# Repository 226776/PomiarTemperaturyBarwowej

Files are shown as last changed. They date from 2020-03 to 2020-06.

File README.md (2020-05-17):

# Pomiar Temperatury Barwowej

## Opis:
Realizacja systemu do pomiaru temperatury bawowej źródeł światła. 
Na system pomiarowy składać się będą: 
- Układ akwizycji danych 
- PC 
- Oprogramowanie 

## Założenia konstrukcyjne:
- metodologia pomiaru: badanie składowych RGB i porównanie ich z charakterystyką ciała doskonale czarnego
- dokładność +-500K
- kalkulacja oraz prezentacja wyniku realizowana przez skrypt/program na PC 
- realizacja układu akwizycji przy użyciu mikrokontrolera z wbudowanym modułem ADC
- zasilanie układu awizycji danych: USB 5V

## Schematic 
- Status: zweryfikowany - płytka wytrawiona
- Środowisko: eagle

## Podgląd
View1
View1

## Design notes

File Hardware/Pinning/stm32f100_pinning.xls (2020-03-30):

PIN | PIN NAME | PIN TYPE | SIGNAL | OPIS | MCU model | Obudowa
1 | Vbat | S | +3V3 | +3V3 | STM32F100C8T6B | LGFP48
2 | PC13-TAMPER-RTC | I/O
3 | PC14-OSC32_IN | I/O
4 | PC15-OSC32_OUT | I/O
5 | OSC_IN | I/O
6 | OSC_OUT | I/O
7 | NRST | I | RESET | Podciągnąc od +3V3. Można dać jakiś przycisk do resetu
8 | Vssa | S | GND | Zasilanie części analogowej GND
9 | Vdda | S | +3V3 | Zasilanie części analogowej +3V3
10 | PA0-WKUP | I/O
11 | PA1 | I/O |  | ANALOG
12 | PA2 | I/O | TX | USART2_TX - wyprowadzenie na goldpiny
13 | PA3 | I/O | RX | USART2_RX - wyprowadzenie na goldpiny
14 | PA4 | I/O | TCSx_OUT | OUT - pin wyjściowy z czujnika TCS3200D
15 | PA5 | I/O |  | ANALOG
16 | PA6 | I/O |  | ANALOG
17 | PA7 | I/O |  | ANALOG
18 | PB0 | I/O |  | ANALOG
19 | PB1 | I/O |  | ANALOG
20 | PB2 | I/O | BOOT1 | BOOT1 - podłączyć przez 1kΩ do GND
21 | PB10 | I/O
22 | PB11 | I/O
23 | Vss_1 | S | GND | GND
24 | Vdd_1 | S | +3V3 | +3V3
25 | PB12 | I/O
26 | PB13 | I/O
27 | PB14 | I/O
28 | PB15 | I/O
29 | PA8 | I/O
30 | PA9 | I/O |  | USART1_TX - można gdzieś wyprowadzić do bootloadera
31 | PA10 | I/O |  | USART1_RX - można gdzieś wyprowadzić do bootloadera
32 | PA11 | I/O
33 | PA12 | I/O
34 | PA13 | I/O | SWDIO | SWDIO - linia danych do programowania. Wyprowadzić na goldpiny
35 | Vss_2 | S | GND | GND
36 | Vdd_2 | S | +3V3 | +3V3
37 | PA14 | I/O | SWCLK | SWCLK - linia zegarowa do programowania. Wyprowadzić na goldpiny
38 | PA15 | I/O
39 | PB3 | I/O
40 | PB4 | I/O
41 | PB5 | I/O | /OE | /OE - pin czujnika TCS3200D
42 | PB6 | I/O | S0 | S0 - pin czujnika TCS3200D
43 | PB7 | I/O | S1 | S1 - pin czujnika TCS3200D
44 | BOOT0 | I | BOOT0 | BOOT0 - podłączyć przez 1kΩ do GND
45 | PB8 | I/O | S2 | S2 - pin czujnika TCS3200D
46 | PB9 | I/O | S3 | S3 - pin czujnika TCS3200D
47 | Vss_3 | S | GND | GND
48 | Vdd_3 | S | +3V3 | +3V3

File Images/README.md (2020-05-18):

View1
View2
View3
View4
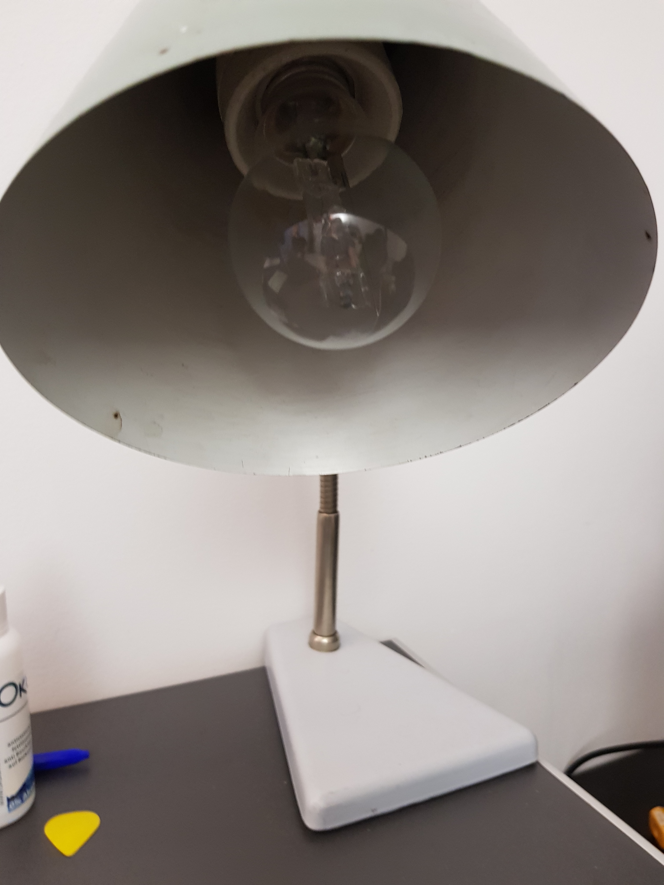
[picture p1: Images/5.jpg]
View5

View6
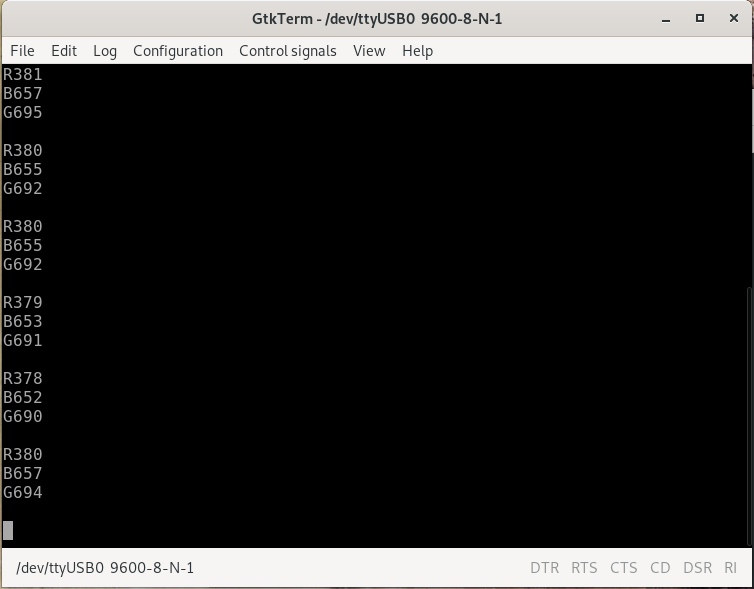
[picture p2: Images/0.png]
View1


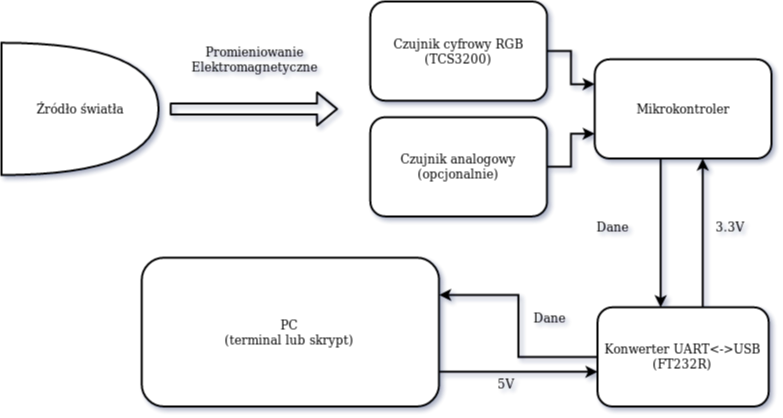
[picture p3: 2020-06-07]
Images/BlockDiagram.png

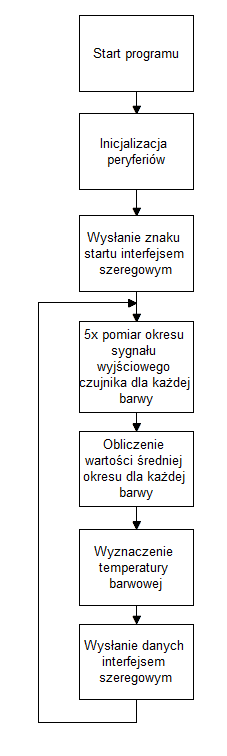
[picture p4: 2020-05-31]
Images/Algorytm.png

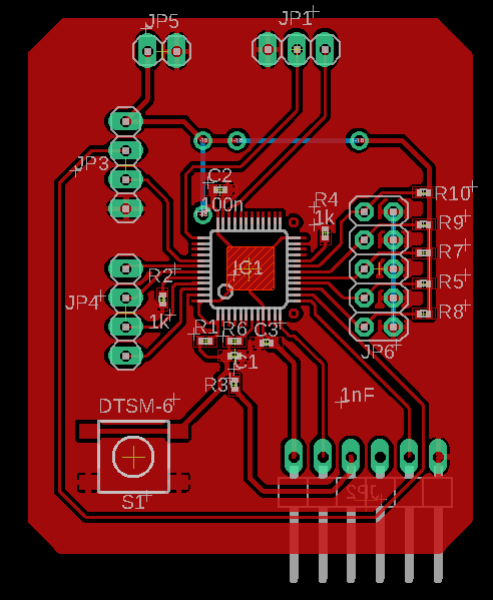
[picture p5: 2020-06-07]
Images/BoardView.png

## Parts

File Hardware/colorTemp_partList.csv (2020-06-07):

Qty | Value | Device | Package | Parts | Description | SPICEPREFIX
1 |  | PINHD-1X2 | 1X02 | JP5 | PIN HEADER
1 |  | PINHD-1X3 | 1X03 | JP1 | PIN HEADER
2 |  | PINHD-1X4 | 1X04 | JP3, JP4 | PIN HEADER
1 |  | PINHD-1X6/90 | 1X06/90 | JP2 | PIN HEADER
1 |  | PINHD-2X5 | 2X05 | JP6 | PIN HEADER
5 |  | R-EU_R0402 | R0402 | R5, R7, R8, R9, R10 | RESISTOR, European symbol | R
1 | 0Ohm | R-EU_R0402 | R0402 | R3 | RESISTOR, European symbol | R
2 | 100n | C-EUC0402 | C0402 | C2, C3 | CAPACITOR, European symbol | C
1 | 10k | R-EU_R0402 | R0402 | R6 | RESISTOR, European symbol | R
2 | 1k | R-EU_R0402 | R0402 | R2, R4 | RESISTOR, European symbol | R
1 | 1nF | C-EUC0402 | C0402 | C1 | CAPACITOR, European symbol | C
1 | 4.7k | R-EU_R0402 | R0402 | R1 | RESISTOR, European symbol | R
1 | DTSM-6 | DTSM-6 | DTSM-6 | S1
1 | STM32F10XCXT6 | STM32F10XCXT6 | TQFP48 | IC1 | ST STM32F101/103 48pin LQFP

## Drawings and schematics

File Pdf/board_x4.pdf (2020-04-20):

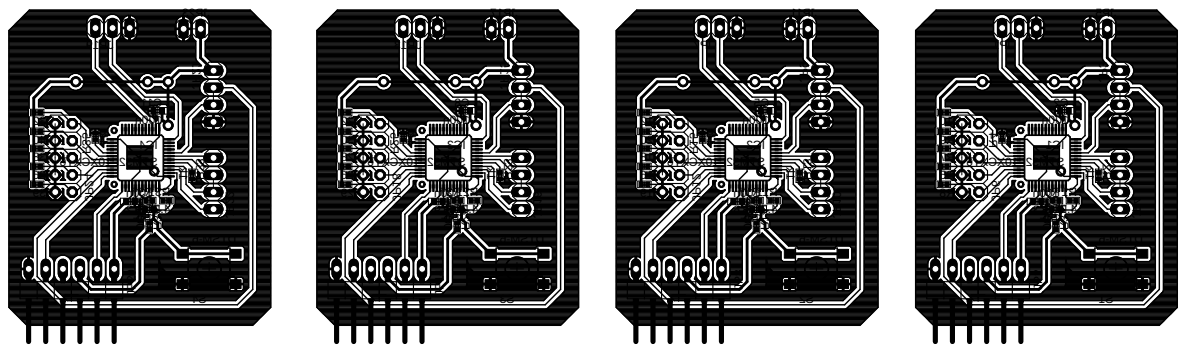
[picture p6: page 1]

Fn1 n001 n001 6TXCX01F23 MTSk7. 4 1k 0Ohm 1k k01 6- MSTD Fn1 n001 n001 6TXCX01F23 MTSk7. 4 1k 0Ohm 1k k01 6- MSTD Fn1 n001 n001 6TXCX01F23 MTSk7. 4 1k 0Ohm 1k k01 6- MSTD Fn1 n001 n001 6TXCX01F23 MTSk7. 4 1k 0Ohm 1k k01 6- MSTD 1 C2 C 3 C1 CI 1PJ JP3 JP4 5PJ JP6 1 R 01 R R2 R3 R4 5 R 6 R 7 R8 R9 R 1S 4 C5 C 6 C2 CI 7PJ JP9 JP10 11PJ JP12 11 R 21 R R13 R14 R15 61 R 71 R 81 R 91 R 02 R 2S 7 C8 C 9 C3 CI 31PJ JP15 JP16 71PJ JP18 12 R 22 R R23 R24 R25 62 R 72 R 82 R 92 R 03 R 3S 01 C11 C 21 C4 CI 91PJ JP21 JP22 32PJ JP24 13 R 23 R R33 R34 R35 63 R 73 R 83 R 93 R 04 R 4S JP2 JP8 JP14 JP20

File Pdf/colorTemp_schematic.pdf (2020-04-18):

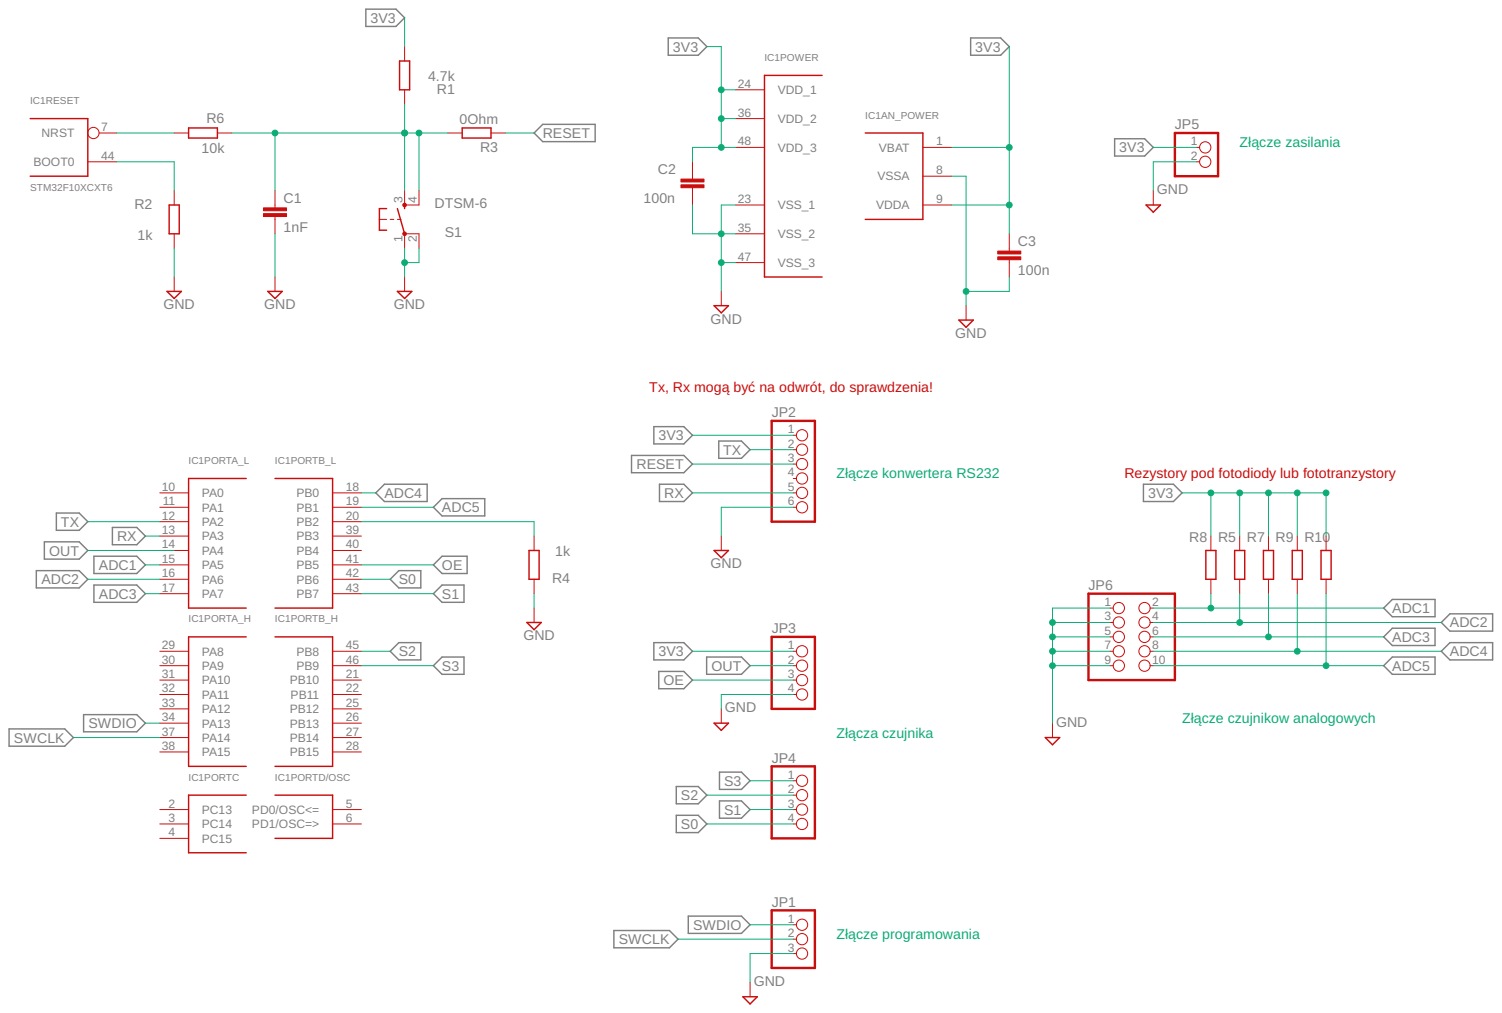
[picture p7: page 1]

Tx, Rx mogą być na odwrót, do sprawdzenia!

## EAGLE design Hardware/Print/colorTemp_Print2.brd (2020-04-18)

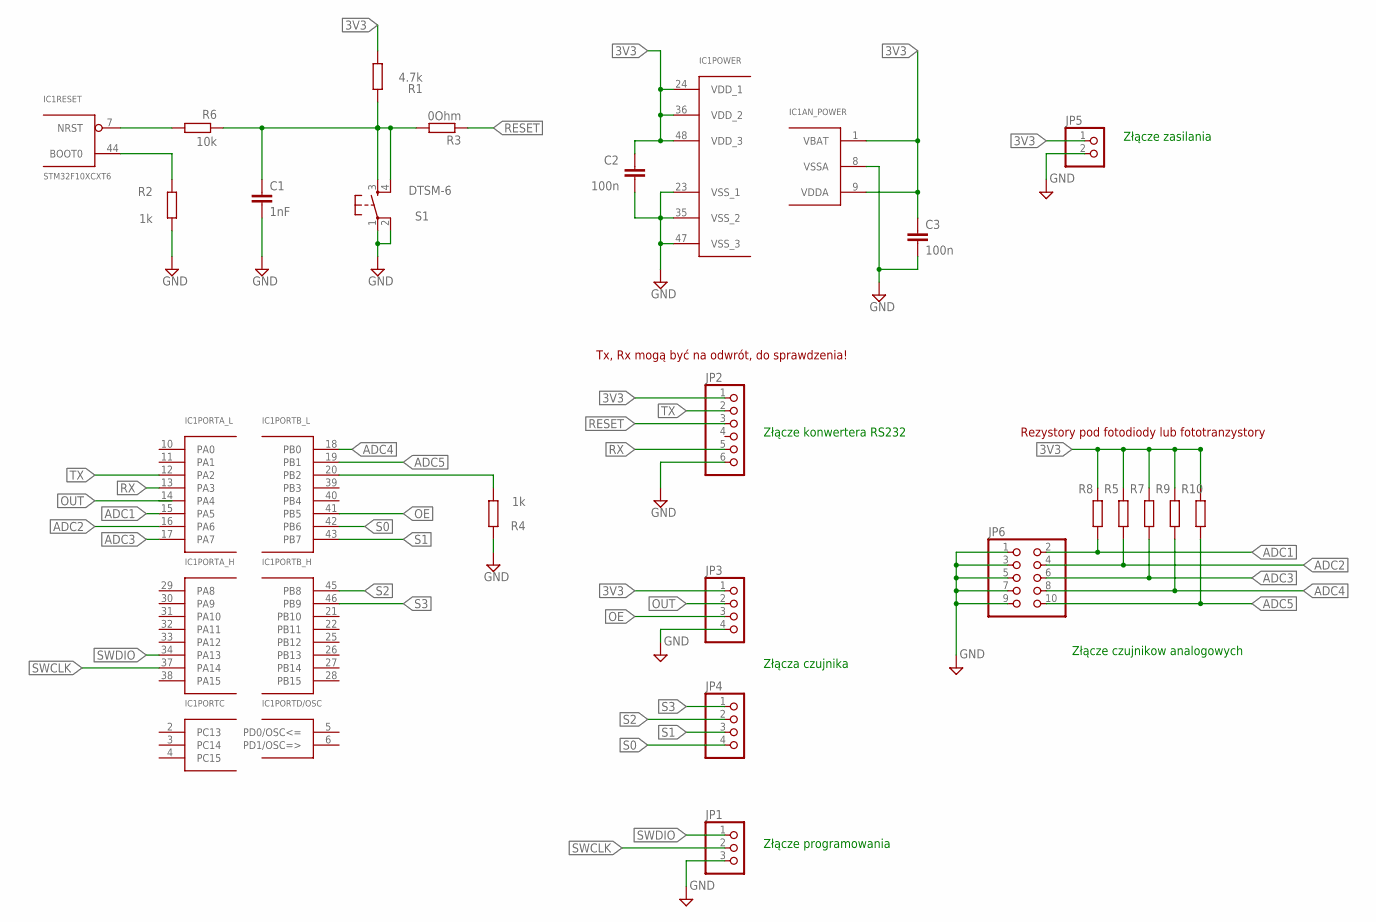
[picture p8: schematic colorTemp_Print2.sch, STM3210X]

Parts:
C1: 1nF; C0402
C2, C3: 100n; C0402
IC1: STM32F10XCXT6; TQFP48
JP1: PINHD-1X3; 1X03
JP2: PINHD-1X6/90; 1X06/90
JP3, JP4: PINHD-1X4; 1X04
JP5: PINHD-1X2; 1X02
JP6: PINHD-2X5; 2X05
R1: 4.7k; R0402
R2, R4: 1k; R0402
R3: 0Ohm; R0402
R5, R7, R8, R9, R10: R-EU_R0402; R0402
R6: 10k; R0402
S1: DTSM-6

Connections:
3V3: C2.1, C3.1, IC1.1 (VBAT), IC1.9 (VDDA), IC1.24 (VDD_1), IC1.36 (VDD_2), IC1.48 (VDD_3), JP2.1, JP3.1, JP5.1, R1.2, R5.1, R7.1, R8.1, R9.1, R10.1
ADC1: IC1.15 (PA5), JP6.2, R8.2
ADC2: IC1.16 (PA6), JP6.4, R5.2
ADC3: IC1.17 (PA7), JP6.6, R7.2
ADC4: IC1.18 (PB0), JP6.8, R9.2
ADC5: IC1.19 (PB1), JP6.10, R10.2
GND: C1.2, C2.2, C3.2, IC1.8 (VSSA), IC1.23 (VSS_1), IC1.35 (VSS_2), IC1.47 (VSS_3), JP1.3, JP2.6, JP3.4, JP5.2, JP6.1, JP6.3, JP6.5, JP6.7, JP6.9, R2.1, R4.1, S1.1, S1.2
unnamed: IC1.44 (BOOT0), R2.2
unnamed: IC1.20 (PB2), R4.2
unnamed: IC1.7 (NRST), R6.2
unnamed: C1.1, R1.1, R3.2, R6.1, S1.3, S1.4
OE: IC1.41 (PB5), JP3.3
OUT: IC1.14 (PA4), JP3.2
RESET: JP2.3, R3.1
RX: IC1.13 (PA3), JP2.5
S0: IC1.42 (PB6), JP4.4
S1: IC1.43 (PB7), JP4.3
S2: IC1.45 (PB8), JP4.2
S3: IC1.46 (PB9), JP4.1
SWCLK: IC1.37 (PA14), JP1.2
SWDIO: IC1.34 (PA13), JP1.1
TX: IC1.12 (PA2), JP2.2

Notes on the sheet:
Tx, Rx mogą być na odwrót, do sprawdzenia!
Złącze konwertera RS232
Złącza czujnika
Złącze programowania
Złącze zasilania
Złącze czujnikow analogowych
Rezystory pod fotodiody lub fototranzystory

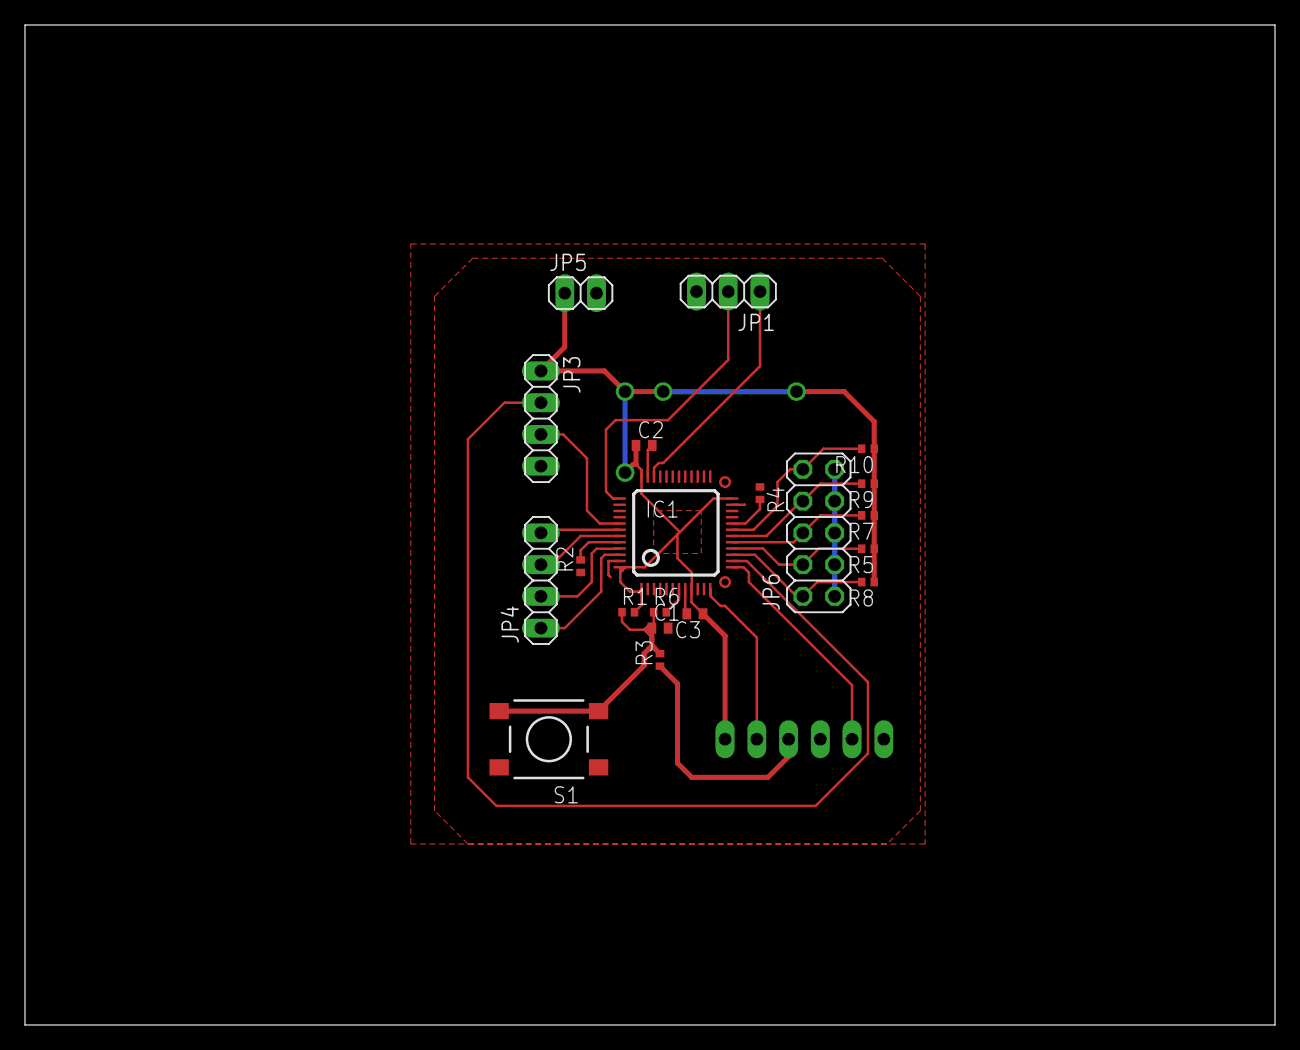
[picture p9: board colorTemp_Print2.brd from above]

Board: 2 copper layers, 100.0 x 80.0 mm, 21 parts (1 on the bottom side), 22 nets.

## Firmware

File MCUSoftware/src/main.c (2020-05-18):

/*
******************************************************************************
File:     main.c
Info:     Generated by Atollic TrueSTUDIO(R) 9.3.0   2020-05-05

The MIT License (MIT)
Copyright (c) 2019 STMicroelectronics

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
******************************************************************************
*/

/* Includes */
#include <stddef.h>
#include "stm32f10x.h"

/* Private macro */
#define nOE_PORT GPIOB
#define nOE GPIO_Pin_5

#define Sx_PORT GPIOB
#define S0 GPIO_Pin_6
#define S1 GPIO_Pin_7
#define S2 GPIO_Pin_8
#define S3 GPIO_Pin_9

#define PWR_DOWN() GPIO_ResetBits(Sx_PORT,S0);GPIO_ResetBits(Sx_PORT,S1);
#define FREQ_SCAL_2p() GPIO_ResetBits(Sx_PORT,S0);GPIO_SetBits(Sx_PORT,S1);
#define FREQ_SCAL_20p() GPIO_SetBits(Sx_PORT,S0);GPIO_ResetBits(Sx_PORT,S1);
#define FREQ_SCAL_100p() GPIO_SetBits(Sx_PORT,S0);GPIO_SetBits(Sx_PORT,S1);

#define OUTPUT_RED() GPIO_ResetBits(Sx_PORT,S2);GPIO_ResetBits(Sx_PORT,S3);
#define OUTPUT_BLUE() GPIO_ResetBits(Sx_PORT,S2);GPIO_SetBits(Sx_PORT,S3);
#define OUTPUT_GREEN() GPIO_SetBits(Sx_PORT,S2);GPIO_SetBits(Sx_PORT,S3);

#define ENABLE_OUTPUT() GPIO_ResetBits(nOE_PORT,nOE);
#define DISABLE_OUTPUT() GPIO_SetBits(nOE_PORT,nOE);

#define SystemCoreClock 8000000 /*HSI frequency*/

/* Private variables */
GPIO_InitTypeDef gpio;
USART_InitTypeDef uart;
EXTI_InitTypeDef exti;
NVIC_InitTypeDef nvic;
TIM_TimeBaseInitTypeDef tim;
uint32_t ticks;
uint32_t scheduler;
uint8_t slope_count;
uint32_t period_meas;
uint32_t RED_values[5];
uint32_t RED_avr;
uint32_t BLUE_values[5];
uint32_t BLUE_avr;
uint32_t GREEN_values[5];
uint32_t GREEN_avr;
uint8_t table_indx;
char str[20];

/* Private function prototypes */
/* Private functions */
void GPIO_init(void);
void UART_init(void);
void RCC_init(void);
void NVIC_EXTI_init(void);
void TIM_init(void);
void delay_ms(uint32_t time_ms);
void send_char(char c);
void send_string(const char* s);
/**
**===========================================================================
**
**  Abstract: main program
**
**===========================================================================
*/
int main(void)
{
	/* PERIPHERAL INITIALIZATION */
	RCC_init();
	GPIO_init();
	UART_init();
	NVIC_EXTI_init();
	TIM_init();

	DISABLE_OUTPUT();
	FREQ_SCAL_2p();
	slope_count = 1;
	period_meas = 0;
	table_indx = 0;

	/*SysTick configuration*/
	if(SysTick_Config(SystemCoreClock / 1000)){
		send_string("E");send_string("\n\r");
		while(1);
	}
	send_string("S");send_string("\n\r");

  /**
  *  IMPORTANT NOTE!
  *  The symbol VECT_TAB_SRAM needs to be defined when building the project
  *  if code has been located to RAM and interrupts are used. 
  *  Otherwise the interrupt table located in flash will be used.
  *  See also the <system_*.c> file and how the SystemInit() function updates 
  *  SCB->VTOR register.  
  *  E.g.  SCB->VTOR = 0x20000000;  
  */
	while(1){
		ENABLE_OUTPUT();
		delay_ms(2);

		/* MEASURE RED */
		OUTPUT_RED();
		delay_ms(2);
		slope_count = 1;
		delay_ms(10);
		RED_values[table_indx] = period_meas;
		slope_count = 0;

		/* MEASURE BLUE */
		OUTPUT_BLUE();
		delay_ms(2);
		slope_count = 1;
		delay_ms(10);
		BLUE_values[table_indx] = period_meas;
		slope_count = 0;

		/* MEASURE GREEN */
		OUTPUT_GREEN();
		delay_ms(2);
		slope_count = 1;
		delay_ms(10);
		GREEN_values[table_indx] = period_meas;
		slope_count = 0;

		delay_ms(100);

		table_indx++;
		if(table_indx > 4){
			DISABLE_OUTPUT();
			/* CALCULATE AVERAGE VALUES */
			RED_avr = (RED_values[0] + RED_values[1] + RED_values[2] + RED_values[3] + RED_values[4]) / 5;
			BLUE_avr = (BLUE_values[0] + BLUE_values[1] + BLUE_values[2] + BLUE_values[3] + BLUE_values[4]) / 5;
			GREEN_avr = (GREEN_values[0] + GREEN_values[1] + GREEN_values[2] + GREEN_values[3] + GREEN_values[4]) / 5;
			table_indx = 0;


			sprintf(str, "%d", RED_avr); /* SEND RED DATA */
			send_string("R");send_string(str);send_string("\n\r");
			sprintf(str, "%d", BLUE_avr); /* SEND BLUE DATA */
			send_string("B");send_string(str);send_string("\n\r");
			sprintf(str, "%d", GREEN_avr); /* SEND GREEN DATA */
			send_string("G");send_string(str);send_string("\n\r");send_string("\n\r");

			delay_ms(1850);
		}



	}
}

/*
 * Interrupt handler.
 * Interrupt generated each rising edge at A4 pin.
 * */
void EXTI4_IRQHandler()
{
	/*First rising edge of the OUT signal*/
	if(slope_count == 1){
		TIM2 -> CNT = 0;
		slope_count = 2;
	/*Second rising edge of the OUT signal - period measurement*/
	}else if (slope_count == 2){
		period_meas = (TIM2 -> CNT);
		slope_count = 1;
	}else if(slope_count != 0){
		slope_count = 1;
	}

	EXTI_ClearITPendingBit(EXTI_Line4);
}

/*
 * SYSTICK used by delay_ms(uint32_t) function.
 * */
void SysTick_Handler()
{
    ticks++;
    //scheduler++;
}

void delay_ms(uint32_t time_ms){
	ticks = 0;
	while(ticks < time_ms);
}



void send_char(char c)
{
    while (USART_GetFlagStatus(USART2, USART_FLAG_TXE) == RESET);
    USART_SendData(USART2, c);
}



void send_string(const char* s)
{
    while (*s)
        send_char(*s++);
}


/* INITIALIZATION FUNCTIONS */
void GPIO_init(){
    /* UART CONFIG */
    /* UART TX */
    GPIO_StructInit(&gpio);
    gpio.GPIO_Pin = GPIO_Pin_2;
    gpio.GPIO_Mode = GPIO_Mode_AF_PP;
    GPIO_Init(GPIOA, &gpio);
    /* UART RX */
    gpio.GPIO_Pin = GPIO_Pin_3;
    gpio.GPIO_Mode = GPIO_Mode_IN_FLOATING;
    GPIO_Init(GPIOA, &gpio);

    /* OUT pin TCS3200D - interrupt generated at this pin */
    GPIO_StructInit(&gpio);
    gpio.GPIO_Pin = GPIO_Pin_4;
    gpio.GPIO_Mode = GPIO_Mode_IPD;
    GPIO_Init(GPIOA, &gpio);

    /* nOE pin TCS3200D - not used. Can be connected to LED pin of TCS3200D module. */
    GPIO_StructInit(&gpio);
    gpio.GPIO_Pin = GPIO_Pin_5;
    gpio.GPIO_Mode = GPIO_Mode_Out_PP;
    GPIO_Init(GPIOB, &gpio);

    /* S0 pin TCS3200D */
    GPIO_StructInit(&gpio);
    gpio.GPIO_Pin = GPIO_Pin_6;
    gpio.GPIO_Mode = GPIO_Mode_Out_PP;
    GPIO_Init(GPIOB, &gpio);

    /* S1 pin TCS3200D */
    GPIO_StructInit(&gpio);
    gpio.GPIO_Pin = GPIO_Pin_7;
    gpio.GPIO_Mode = GPIO_Mode_Out_PP;
    GPIO_Init(GPIOB, &gpio);

    /* S2 pin TCS3200D */
    GPIO_StructInit(&gpio);
    gpio.GPIO_Pin = GPIO_Pin_8;
    gpio.GPIO_Mode = GPIO_Mode_Out_PP;
    GPIO_Init(GPIOB, &gpio);

    /* S3 pin TCS3200D */
    GPIO_StructInit(&gpio);
    gpio.GPIO_Pin = GPIO_Pin_9;
    gpio.GPIO_Mode = GPIO_Mode_Out_PP;
    GPIO_Init(GPIOB, &gpio);


}

/*
 * UART2 initialization
 * */
void UART_init(){
	USART_StructInit(&uart);
	uart.USART_BaudRate = 9600;
	USART_Init(USART2, &uart);

	USART_Cmd(USART2, ENABLE);
}

/*
 * Clock configuration for all peripherals
 * */
void RCC_init(){
	RCC_SYSCLKConfig(RCC_SYSCLKSource_HSI); /* HSI 8MHz is a system clock*/

	RCC -> CFGR &= ~RCC_CFGR_PPRE1; /* APB1 prescaler = 1 */
	RCC -> CFGR &= ~RCC_CFGR_HPRE;  /* AHB prescaler = 1 */

    RCC_APB2PeriphClockCmd(RCC_APB2Periph_GPIOA | RCC_APB2Periph_GPIOB, ENABLE);
	RCC_APB2PeriphClockCmd(RCC_APB2Periph_AFIO, ENABLE);
	RCC_APB1PeriphClockCmd(RCC_APB1Periph_USART2, ENABLE);
	RCC_APB1PeriphClockCmd(RCC_APB1Periph_TIM2, ENABLE);
}

/*
 * Interrupt from TCS3200D OUT pin.
 * Interrupt is generated at each rising edge at OUT pin (A4 pin of the MCU).
 * */
void NVIC_EXTI_init(void){
	EXTI_StructInit(&exti);
	exti.EXTI_Line = EXTI_Line4;
	exti.EXTI_Mode = EXTI_Mode_Interrupt;
	exti.EXTI_Trigger = EXTI_Trigger_Rising;
	exti.EXTI_LineCmd = ENABLE;
	EXTI_Init(&exti);

	nvic.NVIC_IRQChannel = EXTI4_IRQn;
	nvic.NVIC_IRQChannelPreemptionPriority = 0x00;
	nvic.NVIC_IRQChannelSubPriority = 0x00;
	nvic.NVIC_IRQChannelCmd = ENABLE;
	NVIC_Init(&nvic);
}

/*
 * Timer used to measure signal's period at OUT output of TCS3200D sensor.
 * TIM2 is clocked with 1MHz frequency (1us period).
 * */
void TIM_init(void){
	TIM_TimeBaseStructInit(&tim);
	tim.TIM_CounterMode = TIM_CounterMode_Up;
	tim.TIM_Prescaler = 8;
	tim.TIM_Period = 65000 - 1;
	TIM_TimeBaseInit(TIM2, &tim);

	TIM_Cmd(TIM2, ENABLE);
}

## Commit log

2020-04-05 Power supply schematic
    [colorTemp.sch, stm32f100_pinning.xls, stm32f100_pinning.xlsx]
2020-04-05 Schematic STM3210X section
    [colorTemp.sch]
2020-04-05 Supply change
    [colorTemp.sch]
2020-04-05 Schematic Update
    [colorTemp.sch]
2020-04-18 Board in progress
    [colorTemp.brd, colorTemp.sch]
2020-04-18 Board update
    [colorTemp.brd, colorTemp.sch]
2020-05-18 Project CleanUp
    [colorTemp.brd, colorTemp.sch, colorTemp_Print2.brd, colorTemp_Print2.sch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]
2020-05-31 mesuing patterns
    [PomiaryColorTemp.xlsx]
2020-06-07 BoardView.png upload
2020-06-07 Part list
    [colorTemp_partList.csv]
